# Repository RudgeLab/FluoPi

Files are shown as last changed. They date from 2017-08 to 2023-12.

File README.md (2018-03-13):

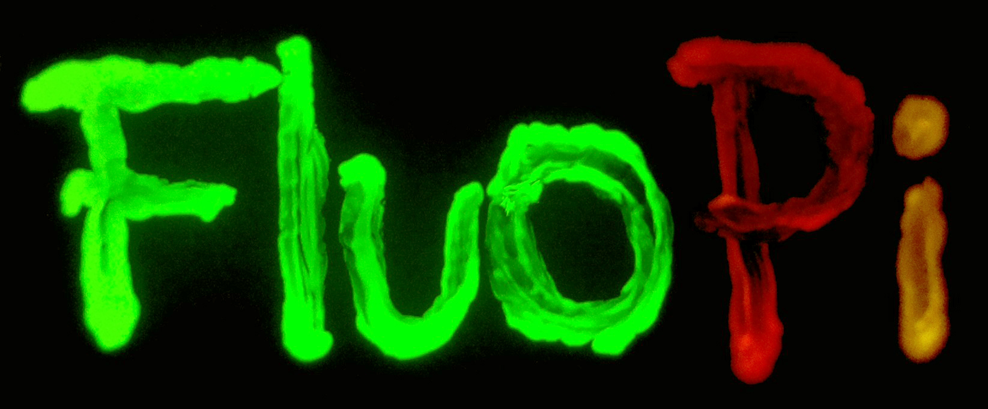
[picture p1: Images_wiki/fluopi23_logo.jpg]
# [][website] 

Hardware design files, code and teaching materials for a low cost and open source fluorescent image registration station.

## Overview

FluoPi is composed of a blue-light transilluminator, an amber acrylic filter and a raspberry camera contained in a black acrylic mainframe. All the hardware is controlled with a Raspberry pi small computer.
With this equipment you are able to:  

* Take images of fluorescent samples ranges from um to cm.
* Perform timelapse assays of up to 3 fluorescent proteins simultaneously
* See electrophoresis gel stained with blue excitable chemicals (such as GelRed or SYBR Safe).

## Getting Started

You can see the full project at [OSF](https://osf.io/dy6p2/)
and a pre-print manuscript at [Biorxiv](https://www.biorxiv.org/content/early/2017/09/27/194324) and peer-reviewed article in [PLoS](http://journals.plos.org/plosone/article?id=10.1371/journal.pone.0187163)

### Prerequisites

To assemble this device you need access to a laser cutter and a 3D printer. You also need a mouse, keyboard and a screen
with HDMI (or hdmi to VGA adaptor) to connect with the Raspberry pi (you can also manage the equipment through SSH or using programs such as [teamviewer](https://pages.teamviewer.com/published/raspberrypi/))

### Installing

All the installation instructions are available on the [wiki page][wiki]

Full documentation and assembly instructions can be found at [Docubricks](http://docubricks.com/viewer.jsp?id=701517893260717056)

### Running the equipment

The equipment has a manual switch and the camera can be controlled with [_camera module commands_](https://www.raspberrypi.org/documentation/usage/camera/raspicam/README.md).
The project includes some python codes (based on [camera python module](https://www.raspberrypi.org/documentation/usage/camera/python/)) to control the hardware:  
* _timelapse.py_ --> to perform timelapse experiments
* _turnON.py_ --> to turn ON the transilluminator
* _turnOFF.py_ --> to turn OFF the transilluminator

### Running the notebooks

Jupyter notebooks are included (Examples/ and Tutorials/) to demonstrate the analysis principles and the use of the fluopi module to analyse time-lapse image data. Sample image data is included in the relevant folders. You can start from these examples, switching the file paths to your data.

## Authors

**Universidad Catolica de Chile**
* Isaac Nuñez - [Prosimio](https://github.com/Prosimio)
* Tamara Matute - [tfmatute](https://github.com/tfmatute)
* Juan Keymner - [Keymer Lab](http://keymerlab.nl/www/?page_id=26)
* Tim Rudge - [Rudge lab](http://rudge-lab.org)
* Fernan Federici - [Federici lab](https://federicilab.org)

[**Backyard Brains Chile**](http://www.backyardbrains.cl/)
* Roberto Pellizzari - [RoHPellizzari](https://github.com/RoHPellizzari)
* Tim Marzullo - [Backyard Brains](http://www.backyardbrains.cl/)

## License

This project is licensed under the MIT License - see the [LICENSE.txt](LICENSE.txt) file for details. Hardware is lincesed under the CERN license.

## FAQs and updates 
Please follow updates, ask questions and check FAQs in this [doc](https://docs.google.com/document/d/1-tSU8xBUZicgM2oZv8TOGw7QUYI85IWkbmjetRthfG8/edit?usp=sharing)

## Acknowledgments

* _Toby Wenzel_ for guidance on Docubricks documentation
* _Tom Baden_  and _Andre Chagas_ for feedback and advice on camera
* _Bernardo Pollak_ for helping out with sequences
* _Douglas Densmore_ for the CIDAR MoClo Parts Kit

* _OpenPlant Fund_ and _Fondecyt_ for providing financial support

[wiki]: https://github.com/SynBioUC/FluoPi/wiki
[website]: https://osf.io/dy6p2/

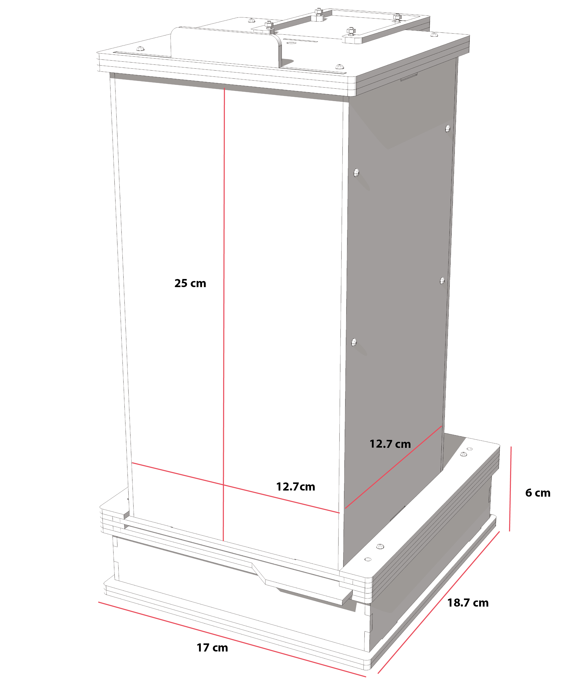
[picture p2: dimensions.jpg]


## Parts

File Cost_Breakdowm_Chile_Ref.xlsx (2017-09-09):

Item | Quantity | Cost Un Chilean Pesos | Cost x1 (USD) | Total cost (USD) | Reference | details
Rapsberry PI model 3 with 16Gb SD card | 1 | $41500 | $62.88 | $62.88 | http://olimex.cl/en_US/shop/product/raspberry-pi-model-3-with-16gb-memory-noobs-system-preloaded-21545?category=415
Power supply RPI | 1 | $8590 | $13.02 | $13.02 | http://olimex.cl/en_US/shop/product/transformador-para-raspberry-pi-5v-2-5amp-21421?category=415&page=2
M3 - 10 mm Length Screw | 20 | $9.81 | $0.01 | $0.30 | www.fijaciones.com (http://www.fijaciones.com/mr/pernos_tuercas_golillas/perno_cocina_cabeza_binding.asp)
M3 - 15 mm Length Screw | 6 | $11.35 | $0.02 | $0.10 | www.fijaciones.com (http://www.fijaciones.com/mr/pernos_tuercas_golillas/perno_cocina_cabeza_binding.asp)
M3 - 20 mm Length Screw | 6 | $5.95 | $0.01 | $0.05 | www.fijaciones.com (http://www.fijaciones.com/mr/pernos_tuercas_golillas/perno_cocina_cabeza_binding.asp)
M3 Hex Nut | 32 | $8.71 | $0.01 | $0.42 | www.tecbolt.cl (http://www.tecbolt.cl/mr/pernos_tuercas_golillas/pdf/tuerca_cocina_hexagonal.pdf)
M4 - 25 mm Length Screw | 6 | $18.90 | $0.03 | $0.17 | www.fijaciones.com (http://www.fijaciones.com/mr/pernos_tuercas_golillas/perno_cocina_cabeza_binding.asp)
M4 - 40 mm Length Screw | 1 | $33.03 | $0.05 | $0.05 | www.fijaciones.com (http://www.fijaciones.com/mr/pernos_tuercas_golillas/perno_cocina_cabeza_binding.asp)
M4 - 50 mm Length Screw | 4 | $31.34 | $0.05 | $0.19 | www.fijaciones.com (http://www.fijaciones.com/mr/pernos_tuercas_golillas/perno_cocina_cabeza_binding.asp)
M4 Hex Nut | 11 | $8.93 | $0.01 | $0.15 | www.tecbolt.cl (http://www.tecbolt.cl/mr/pernos_tuercas_golillas/pdf/tuerca_cocina_hexagonal.pdf)
3D prints (all together) | 1 | $2000 | $3.03 | $3.03 | Calculated based on ABS cost in grams of materials
80 x 50 cm Black Acrylic Plate 3mm | 2 | $12300 | $18.64 | $37.27 | www.norglas.cl/
30 x 30 cm Transparent Acrylic Plate 3mm | 1 | $2315 | $3.51 | $3.51 | www.norglas.cl/
30 x 30 cm Amber Acrylic Plate 3mm | 1 | NA | $7.84 | $7.84 | https://www.mcmaster.com/#catalog/123/3632/=191et4m | 85635K462 Optically Fluorescent Cast Acrylic, 1/8" Thick, 12" X 12", Amber
30 x 30 cm Blue Acrylic Filter 3mm | 1 | NA | $9.34 | $9.34 | http://www.acrylite.net/product/acrylite/en/Pages/default.aspx | ACRYLITE® extruded (FF), sheet, Blue 5C028 GT
Paper Diffusor | 1 | $1000 | $1.52 | $1.52
RPi Camera (B), Adjustable-Focus | 1 | NA | $17.59 | $17.59 | http://www.waveshare.com/product/mini-pc/raspberry-pi/cameras/rpi-camera-b.htm
PCB | 1 | $7500 | $11.36 | $11.36 | https://www.seeedstudio.com
Blue LED | 100 | NA | $0.54 | $54.00 | https://www.superbrightleds.com/moreinfo/through-hole/5mm-blue-led-120-degree-viewing-angle-flat-tipped-1200-mcd/265/
Switch | 1 | $200 | $0.30 | $0.30 | https://www.digikey.com/product-detail/en/zf-electronics/SRB22A2FBBNN/CH755-ND/446021
Power Plug | 1 | $200 | $0.30 | $0.30 | www.casaroyal.cl/Casa/Royal
24V Power Source | 1 | $12990 | $19.68 | $19.68 | www.casaroyal.cl/Casa/Royal
Resistor 330 ohm | 20 | NA | $0.03 | $0.60 | https://www.digikey.com/product-detail/en/stackpole-electronics-inc/CF14JT330R/CF14JT330RCT-ND/1830338
Resistor 1 kohm | 1 | NA | $0.03 | $0.03 | https://www.digikey.com/product-detail/en/stackpole-electronics-inc/CF14JT1K00/CF14JT1K00CT-ND/1830350
Digital Control Cable | 1 | $1000 | $1.52 | $1.52
TIP122 transistor | 1 | $400 | $0.61 | $0.61 | www.casaroyal.cl/Casa/Royal
Total |  |  |  | $245.22

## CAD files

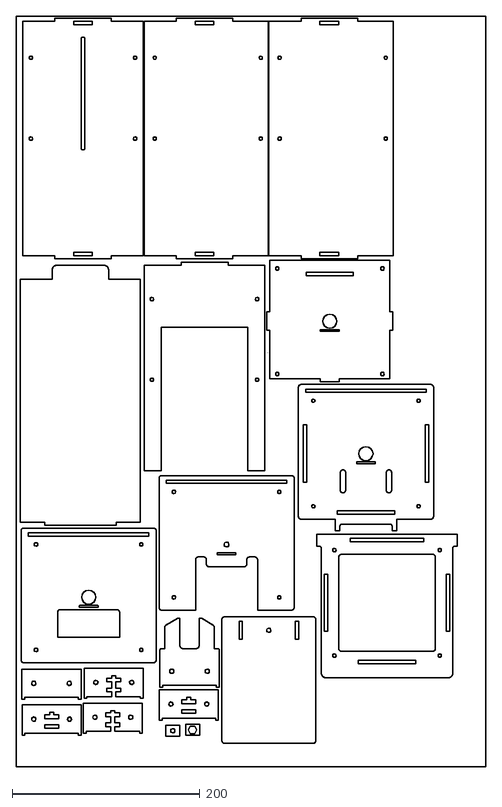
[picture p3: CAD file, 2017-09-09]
Hardware_design_files/2D/ReadytoCut/Fluopi - Black Ac - 3mm - 800x500 mm.dxf
500.0 x 800.0

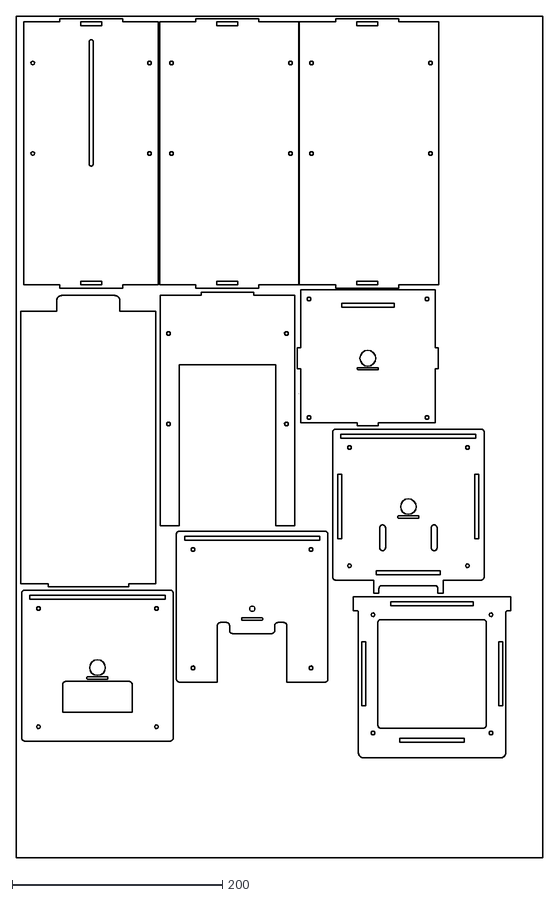
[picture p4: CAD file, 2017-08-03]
Hardware_design_files/2D/single_files/MF6-3 Final Cut - Top Module Black Acrilic.dxf
500.0 x 800.0

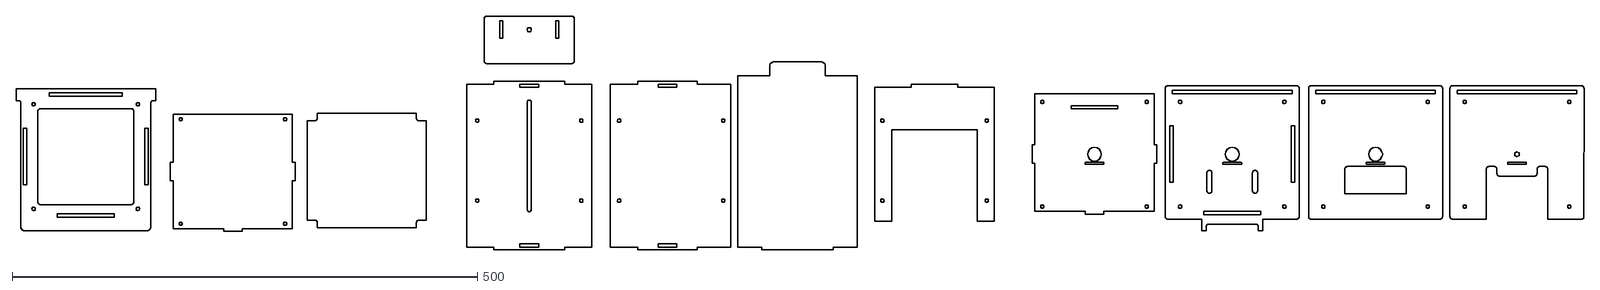
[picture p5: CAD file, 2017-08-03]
Hardware_design_files/2D/single_files/short_version/MF6-3 Final Cut - Short TopMod.dxf
1684.9 x 251.2

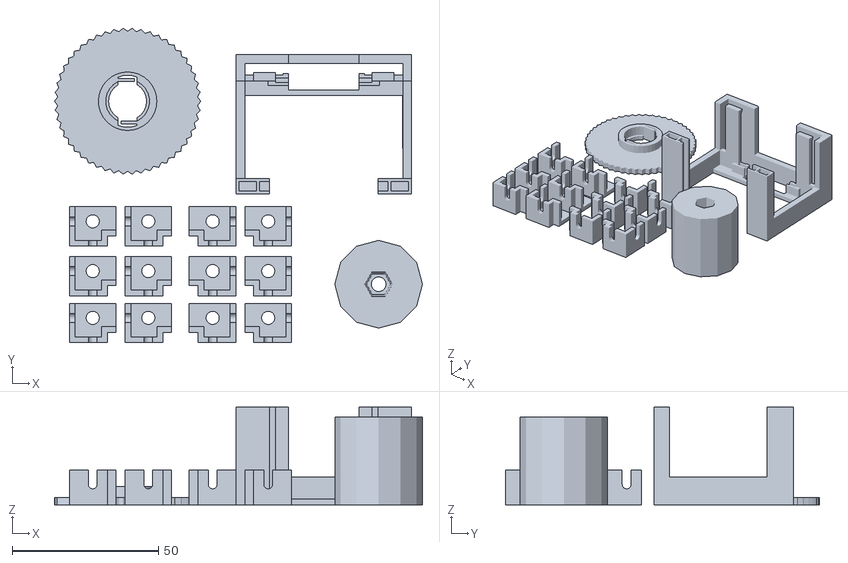
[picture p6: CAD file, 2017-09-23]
Hardware_design_files/3D/Readytoprint/Fluopi - All 3D print parts.stl
125.8 x 107.5 x 33.5

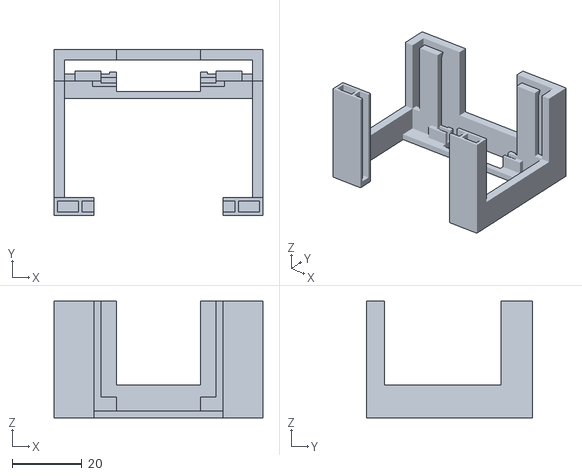
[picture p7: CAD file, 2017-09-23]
Hardware_design_files/3D/single_files/MF6-3 Final Cut - Raspberry Cam Adaptor.stl
60.0 x 47.6 x 33.5

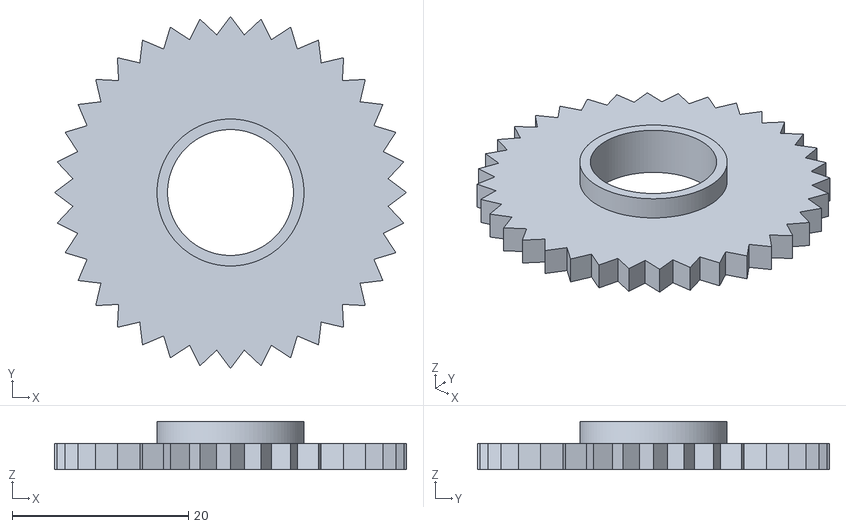
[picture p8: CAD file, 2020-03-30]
PostManuscript_updates_and_FAQs_other_versions/Hardware/STLs/M12_focus_knob.stl
40.0 x 40.0 x 5.50

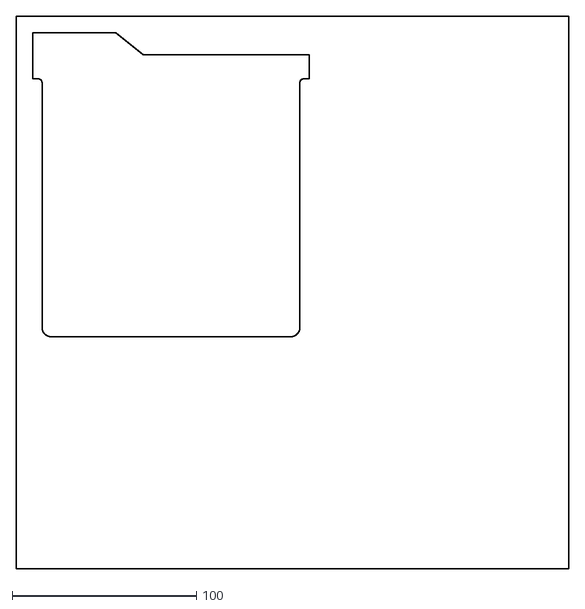
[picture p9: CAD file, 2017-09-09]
Hardware_design_files/2D/ReadytoCut/Fluopi - Blue Ac - 3mm - 300x300 mm.dxf
300.0 x 300.0

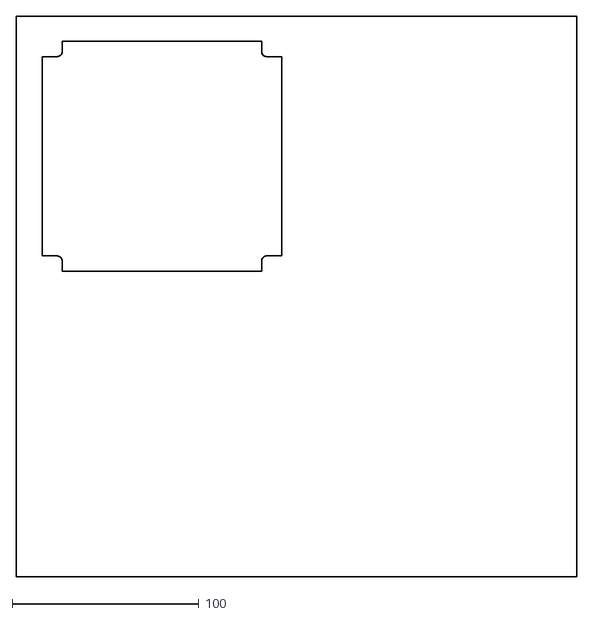
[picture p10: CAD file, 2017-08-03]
Hardware_design_files/2D/single_files/MF6-3 Final Cut - Paper Diffusor.dxf
300.0 x 300.0

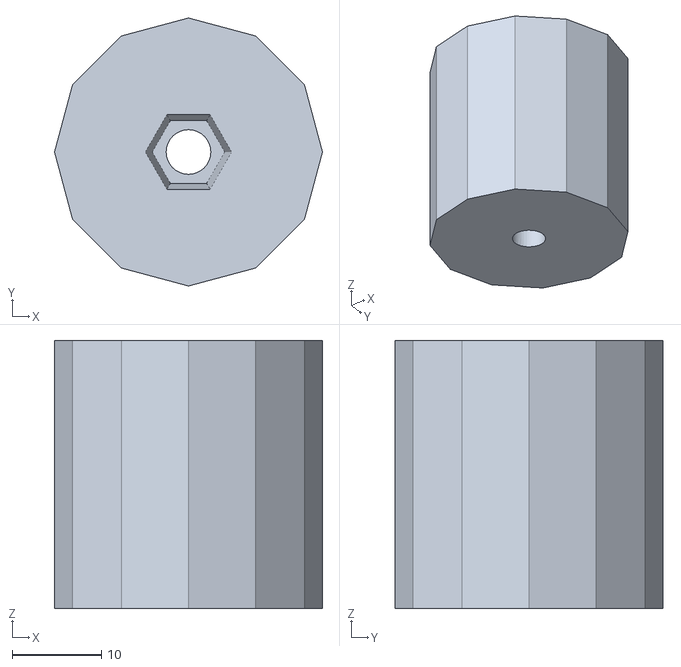
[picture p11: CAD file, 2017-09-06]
Hardware_design_files/3D/single_files/MF6-3 Locking Knob.stl
30.0 x 30.0 x 30.0

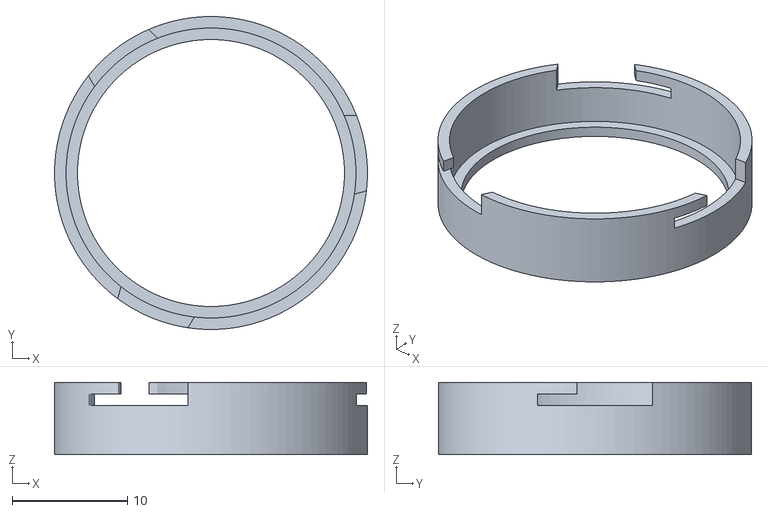
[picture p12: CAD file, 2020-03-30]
PostManuscript_updates_and_FAQs_other_versions/Hardware/STLs/circle_filter_holder.stl
27.2 x 27.2 x 6.30

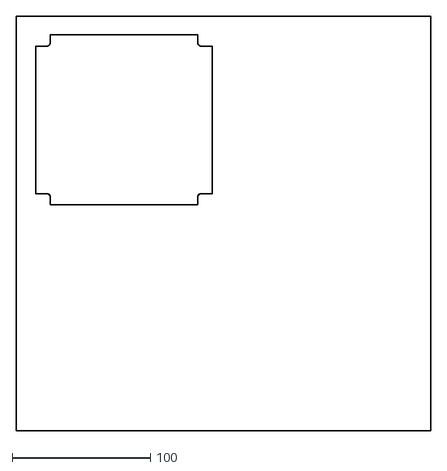
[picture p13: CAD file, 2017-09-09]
Hardware_design_files/2D/ReadytoCut/Fluopi - Paper Diffusor - 300x300 mm.dxf
300.0 x 300.0

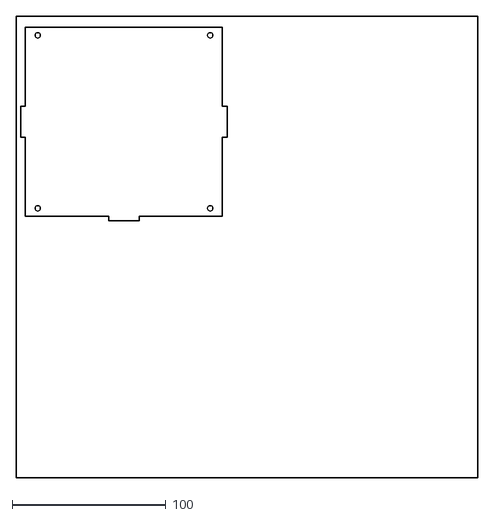
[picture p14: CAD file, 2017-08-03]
Hardware_design_files/2D/single_files/MF6-3 Final Cut - Top Module Transparent Acrilic.dxf
300.0 x 300.0

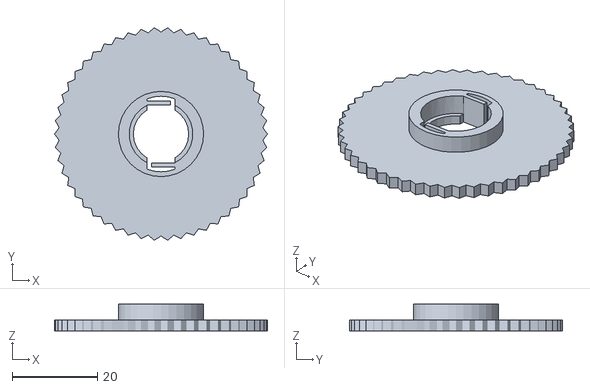
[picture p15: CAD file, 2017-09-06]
Hardware_design_files/3D/single_files/Focus Knob.stl
50.0 x 49.9 x 6.30

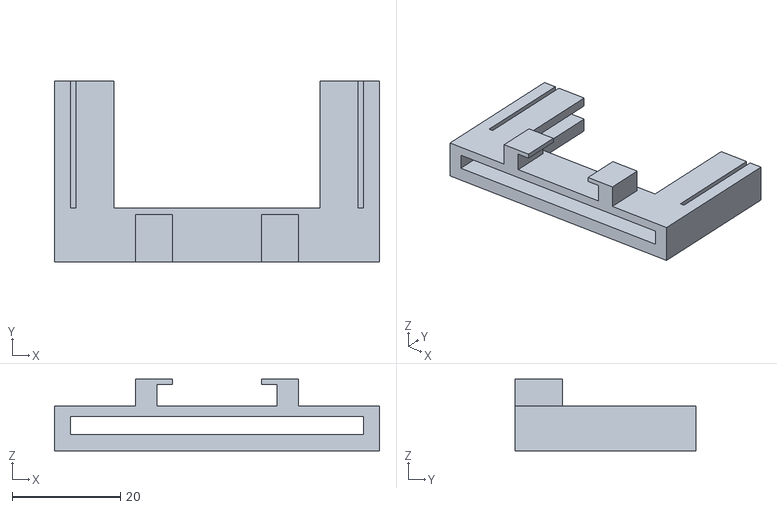
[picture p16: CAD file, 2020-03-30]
PostManuscript_updates_and_FAQs_other_versions/Hardware/STLs/Flat_cam_holder_RPIV2cam.stl
60.0 x 33.5 x 13.2

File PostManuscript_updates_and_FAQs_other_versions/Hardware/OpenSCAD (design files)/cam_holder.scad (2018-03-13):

/*
    Fernán Federici 2017 (CC BY 4.0; https://creativecommons.org/licenses/by/4.0/) 
 
    With this code you can make a camera adapter for RPI camera from waveshare (http://www.waveshare.com/product/mini-pc/raspberry-pi/cameras/rpi-camera-b.htm) and for V2 RPI camera (https://www.raspberrypi.org/products/camera-module-v2/)
 
*/

/////This code needs a lot of clean up and reorganization but it works//////////edits would be very welcome :) ////////////
 
x=60;//frontal width
y=47;//height 33+9+5
z=33.5; // depth
filter_x=43.7;
filter_y=31.4;
filter_z=3;
bed_x=54;
bed_y=3;
bed_z=100;
arm=5;
focus_space=20; // enough distance for lens focus adjustment
holder_x=54;//acrylic bed width to fit into holder
holder_y=3;//acrylic bed thickness to fit into holder, normally 3mm acrylic
$fn=100;
fudge=0.1; // to fix error in rendering leaving thin wall...help me!
int_gap=17.5; 
camera_type=0; //0 for waveshare camera (32x32mm); 1 for V2 RPI camera (25x24x9)
china_spacex= 24.3;
V2_spacex= 18;
waveshare_cam_x=32.2;
waveshare_cam_y=1.5; //thickness
waveshare_cam_z=32.2;
RPIV2_cam_x=25;
RPIV2_cam_y=1.5; //thickness
RPIV2_cam_z=24;


module cam_holder_base() {
    difference(){
    cube([x,y,z], center=true);
           translate([0,(y/2)-arm/2,2]) rotate([90,0,0])  cube([filter_x,filter_y,filter_z], center=true);
           translate([0,0,8])  color("blue") cube([filter_x-4,y+fudge,z*0.9], center=true);
           translate([0,(y/2)-(focus_space/2+arm),0])  color("Red")  cube([(x-arm),focus_space,z+fudge], center=true);
           translate([0,-((y/2)-arm/1.5),0]) color ("pink") cube([holder_x+fudge,holder_y,z+fudge], center=true);
           translate([0,-arm,arm+fudge]) color ("purple")  cube([(x-arm)+fudge,focus_space,(z-arm*2)+fudge], center=true);
           translate([0,-arm*1.5,-arm/2+fudge]) color ("yellow")  cube([int_gap,y/2,(z-arm*2)+fudge], center=true);
           translate([0,-arm*2,-arm/2+fudge]) color ("black")  cube([filter_x-4,arm*2,(z-arm*2)+fudge], center=true);
    }
}
       
module waveshare_cam() {
           translate([0,-((y/2)-arm/.75),0]) color ("red")  cube([china_spacex,arm*1.5,z+fudge], center=true);
           translate([0,-((y/2)-arm/.75),arm/2+fudge]) color ("yellow")  cube([waveshare_cam_x,waveshare_cam_y,z+fudge], center=true);
 }
  
module RPIV2_cam() {
       //difference() {
           //cam_holder_base();
           translate([0,-((y/2)-arm/.75),0]) color ("red")  cube([V2_spacex,arm*1.5,z+fudge], center=true);
           translate([0,-((y/2)-arm/.75),arm/2+fudge]) color ("yellow")  cube([RPIV2_cam_x,RPIV2_cam_y,RPIV2_cam_z+fudge], center=true);
     }     
     
module cam_holder(camera_type) {

     if(camera_type==0)
           difference() {
           cam_holder_base();
               waveshare_cam() ;
           }          
     else 
           difference() {
           cam_holder_base();
               RPIV2_cam();
           }
       }     
cam_holder(1); 

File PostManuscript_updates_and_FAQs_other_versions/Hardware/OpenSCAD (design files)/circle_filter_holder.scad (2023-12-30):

/*
    
    With this code you can make a filter holder to attach it to the lens focus wheel used for the camera in the FluoPi project.
    
    Isaac Núñez 2020 (CC BY 4.0; https://creativecommons.org/licenses/by/4.0/) 
 
*/

////////////////
// Parameters //


ri = 12.6;   //filter radius
side_thick = 1 ;
filter_thick = 3;
filter_free_space = 0.5;
bottom_thick = 0.8;
sheet = 1; // sheet tickness to support the filter

rb = ri-sheet; // internal hole radius
re = ri +side_thick; // External radius

h_fs = filter_thick +filter_free_space + bottom_thick; //base filter support heigh

// HQ camera
r_hq = 15; // HQ camera radius
h_ring = 3; // Height of the ring attached to the camera

// RPI V2 camera


// Clamp support system for waveshare camera
h_clam = 2;
free_clam_space = 10;
angles1 = [0,120,240];
angles2 = [15,135,255];

h_WS = h_fs + h_clam; // for waveshare

////////////////////////////////////

module clam_space(length, wide, thickness, angles){

    for(ang = angles){
       rotate([0,0,ang])
       translate([length/2, 0, 0])
       cube([length, wide, thickness], center = true);
    }
}



////////////////////////
// Create the holder //

module filter_support(h){
    difference(){
    linear_extrude(height = h, center = true, convexity = 10, twist = 0,$fn = 100)
    circle(re);
    
    translate([0,0,bottom_thick])
    linear_extrude(height = h, center = true, convexity = 10, twist = 0,$fn = 100)
    circle(ri);
        
    translate([0,0,-bottom_thick])          linear_extrude(height = h, center = true, convexity = 10, twist = 0,$fn = 100)
    circle(rb);
    }
}

module fsup_WS_clamp(h){
    difference(){
        
        filter_support(h);
        
        // Clamp system
        translate([0,0,h/2-h_clam/2 - h_clam/4]) 
        clam_space(re*1.5, free_clam_space ,h_clam/2, angles1);

        translate([0,0,h/2-0.8*h_clam/2.1])  
        intersection() {

            clam_space(re*1.5, free_clam_space ,h_clam*0.8, angles1);

            clam_space(re*1.5, free_clam_space ,h_clam*0.8, angles2);
        }
    }
}

module fsup_HQ(h){
    h_total = h + bottom_thick + h_ring;
    
    difference(){
        union(){
            filter_support(h);
            
            //union ring
            translate([0,0,(h-bottom_thick)/2])
            cylinder(h=bottom_thick, r=r_hq+side_thick, $fn=100, center =true);
            
            //ring attached to HQ camera
            translate([0,0,(h+h_ring)/2])
            difference(){
                cylinder(h=h_ring, r=r_hq+side_thick, $fn=100, center =true);
                cylinder(h=h_ring, r=r_hq, $fn=100, center =true);
            }
            }
    translate([0,0,bottom_thick+h/2])          
    cylinder(h=h_total, r=ri, $fn=100, center =true);  
    }

}

module fsup_rpiv2(h){
    union(){
        filter_support(h);
    
    }
}

// Uncomment the module you wanna generate
//fsup_WS_clamp(h_WS);
//filter_support(h_WS);
fsup_HQ(h_fs);

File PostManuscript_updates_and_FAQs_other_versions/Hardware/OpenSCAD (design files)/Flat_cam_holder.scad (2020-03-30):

/*
    With this code you can make a camera holder for RPI camera from waveshare (http://www.waveshare.com/product/mini-pc/raspberry-pi/cameras/rpi-camera-b.htm) or for V2 RPI camera (https://www.raspberrypi.org/products/camera-module-v2/)
    
    The code was modified from Fernán Federici 2017 version.
    
    This is licensed under the Creative Commons - Attribution license (CC BY 4.0)
    Isaac Núñez 2020.
 
*/

///////////////////////
// Fluopi parameters

holder_x=54;//acrylic bed width to fit into holder
holder_z=3*1.1;//acrylic bed thickness to fit into holder, normally 3 mm acrylic. 1.1 correction factor applied to surpass acrylic manufacture variations.

////////////////////////
// Defined by the user

// Base holder parameters

sca_thick_up = 3; // holder scafold thickness
sca_thick_side = 3; // holder scafold thickness
sca_thick_down = 2; // holder scafold thickness
sca_deep = 10;  // holder scafold back deep, it have to be shorter than the distance to the screws in the camera PCB (14 mm aprox)
sca_arms_width = 11; // holder scafold arms width

sca_arms_space = 1;  // space attach relaxation


sca_trans = (sca_thick_up - sca_thick_down)/2; // translate the holder space to achieve the desired up and down thicknes

scafold_x = holder_x + 2*sca_thick_side;
scafold_y = 33.5; // depth
scafold_z = holder_z + sca_thick_up + sca_thick_down;


//camera holder parameters

side_thick = 2; //side support thickness
bottom_thick = 1; // bottom support thickness
back_thick = 2; // back support thickness

/////////////////////
//  Camera details:

////////////////////////////////
// Waveshare Chinesse camera //
///////////////////////////////
waveshare_cam_x=32.2 + 1; // 1mm of error
waveshare_cam_y=32.2; 
waveshare_cam_z=1.5*1.1;//thickness
WS_hold_x = 5.1 - 0.3;    // space between border and cable conector. 0.3 the security factor
WS_hold_y = 4.5 - 0.3;  // space between border and resistor. 0.3 the security factor

///////////////////
// RPI V2 camera //
///////////////////

RPIV2_cam_x = 25 + 1 ; // 1mm of error
RPIV2_cam_y = 24; 
RPIV2_cam_z = 1 + 0.1; // PCB thickness, 0.1 mm of error
RPIV2_connec_x = 22; // cable conector length
RPIV2_connec_z = 2.7+ 0.1; // cable conector thikness, 0.1 mm error

RPIV2_sensor_x = 16 + 0.5; // sensor base length (8.5 mm) or adaptor lenght + 0.5 mm error

V2_hold_x =(RPIV2_cam_x - RPIV2_sensor_x)/2 - 0.3;    // space between camera border and sensor base. 0.3 the security factor
V2_hold_y = 7 - 0.2;  // space between border and PCB first obstacle (sensor base or electronic componentes). 0.2 security value.


module cam_holder_base() {
    
    difference(){
    cube([scafold_x,scafold_y,scafold_z], center=true);
     translate([0,0,sca_trans])cube([holder_x,scafold_y*1.1,holder_z], center=true);
     translate([0,sca_deep/2,0])cube([scafold_x - 2*sca_arms_width,scafold_y - sca_deep,scafold_z], center=true);
     translate([holder_x/2-sca_arms_space/2,sca_deep/2,scafold_z/2])cube([sca_arms_space,scafold_y - sca_deep,scafold_z], center=true);
     translate([-holder_x/2+sca_arms_space/2,sca_deep/2,scafold_z/2])cube([sca_arms_space,scafold_y - sca_deep,scafold_z], center=true);
        
        }      
}

module camera_mount(camera){

    if(camera == "waveshare"){
            cam_x = waveshare_cam_x;
            cam_y = waveshare_cam_y;
            cam_z = waveshare_cam_z;
            hold_x = WS_hold_x;
            hold_y = WS_hold_y;
    
        support_z = cam_z+bottom_thick;
        support_y = hold_y + back_thick;
        translate([0,-scafold_y/2 + support_y/2,scafold_z/2+support_z/2])difference(){cube([cam_x+2*side_thick,support_y,support_z], center=true);
            translate([0,back_thick/2,-bottom_thick/2])cube([cam_x,hold_y,cam_z], center=true);
            translate([0,0,0])cube([cam_x - 2*hold_x,support_y,support_z], center=true);
    }
    }
    
    else if(camera == "RPIV2"){
            cam_x = RPIV2_cam_x;
            cam_y = RPIV2_cam_y;
            cam_z = RPIV2_cam_z;
            hold_x = V2_hold_x;
            hold_y = V2_hold_y;
            base_space = RPIV2_connec_x+0.2;
         
    support_z = cam_z+bottom_thick + RPIV2_connec_z;
    support_y = hold_y + back_thick;
    translate([0,-scafold_y/2 + support_y/2,scafold_z/2+support_z/2])difference(){cube([cam_x+2*side_thick,support_y,support_z], center=true);
        translate([0,back_thick/2,-bottom_thick/2 + RPIV2_connec_z/2])cube([cam_x,hold_y,cam_z], center=true); // camera PCB hole
        translate([0,0,-bottom_thick/2])cube([base_space,support_y,support_z-bottom_thick], center=true); // base hole
                translate([0,0,(support_z-bottom_thick)/2])cube([RPIV2_sensor_x,support_y,bottom_thick], center=true); // camera hole
    }
    }
    
}


cam_holder_base();

//uncomment the one you pretend to use

camera_mount("RPIV2");
//camera_mount("waveshare");

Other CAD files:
Hardware_design_files/2D/ReadytoCut/Fluopi - Transp Ac - 3mm - 300x300 mm.dxf
Hardware_design_files/2D/single_files/MF6-3 Final Cut - Dimensiones.dxf
Hardware_design_files/3D/single_files/MF6-3 Final Cut - Spacer L.stl
PostManuscript_updates_and_FAQs_other_versions/Hardware/STLs/Flat_cam_holder_WScam.stl
PostManuscript_updates_and_FAQs_other_versions/Hardware/OpenSCAD (design files)/Focus_knob_FilterAttach.scad
Hardware_design_files/2D/ReadytoCut/Fluopi - Amber Ac - 3mm - 300x300 mm.dxf
Hardware_design_files/2D/single_files/MF6-3 Final Cut - Filter Amber Acrilic.dxf
Hardware_design_files/2D/single_files/MF6-3 Final Cut - Filter Blue Acrilic.dxf
Hardware_design_files/2D/single_files/MF6-3 Final Cut - Raspberry Adaptor Acrilic.dxf
Hardware_design_files/2D/single_files/MF6-3 Final Cut - Vert Bed Module Black Acrilic.dxf
Hardware_design_files/3D/single_files/MF6-3 Final Cut - Spacer R.stl
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

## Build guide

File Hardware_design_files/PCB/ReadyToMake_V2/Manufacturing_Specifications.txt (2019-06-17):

Manufacturing specifications:

PCB size: ~ 170 mm x 125 mm 
Track width: 1.0 mm
N° layers: 2
Material: FR-4
Glass Transition Temperature: TG 130-140
Thickness: 1.6 mm
min Track/Spacing: 6/6mil
Min Hole size: 1.0 mm (choose something lower than 1.0 mm)
SilkScreen: White
Finished Copper: bigger than 1 oz Cu

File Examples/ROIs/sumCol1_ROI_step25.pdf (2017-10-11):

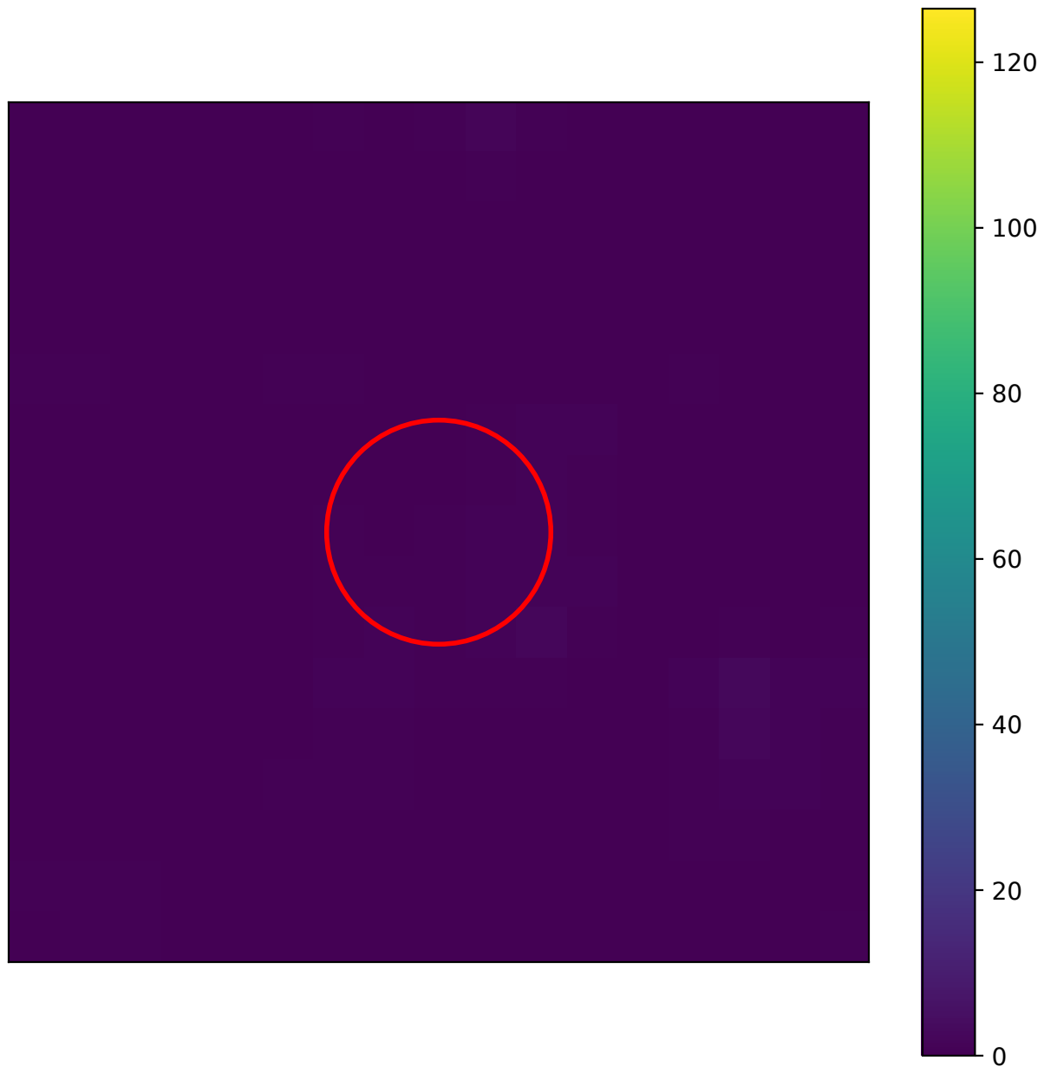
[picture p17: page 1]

0

20

40

60

80

100

120

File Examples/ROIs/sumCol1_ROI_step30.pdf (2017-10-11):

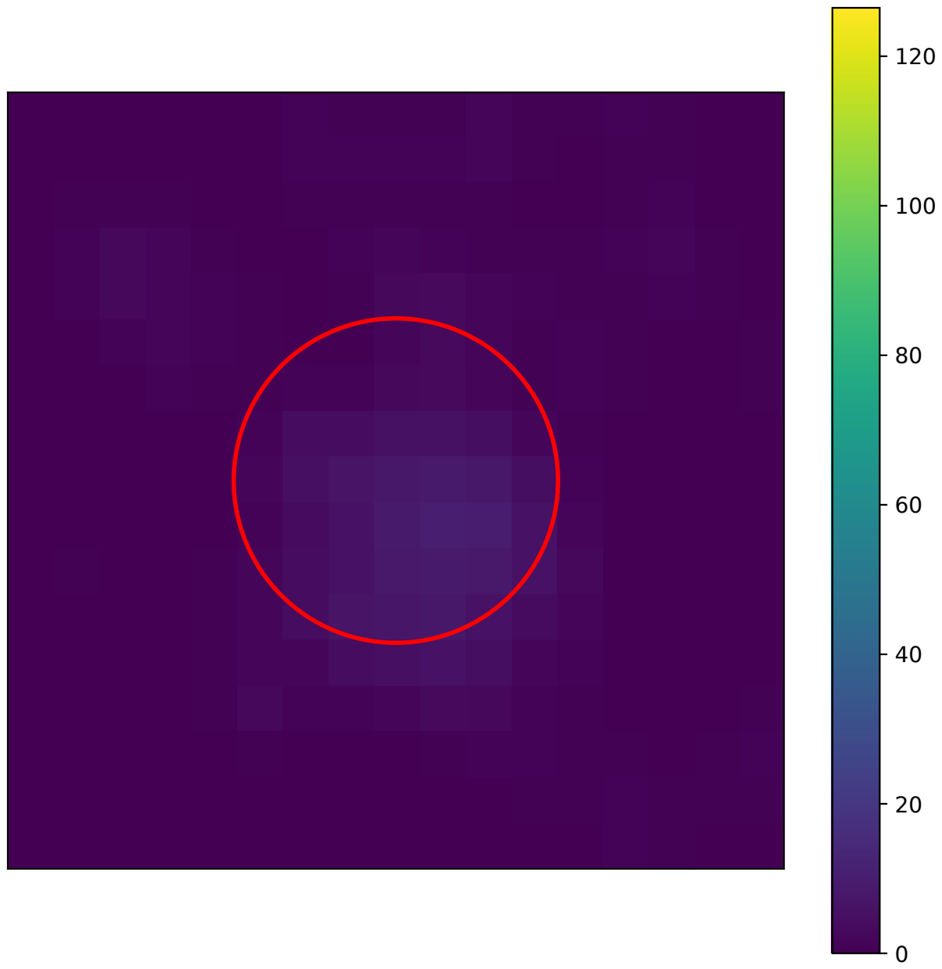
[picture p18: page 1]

0

20

40

60

80

100

120

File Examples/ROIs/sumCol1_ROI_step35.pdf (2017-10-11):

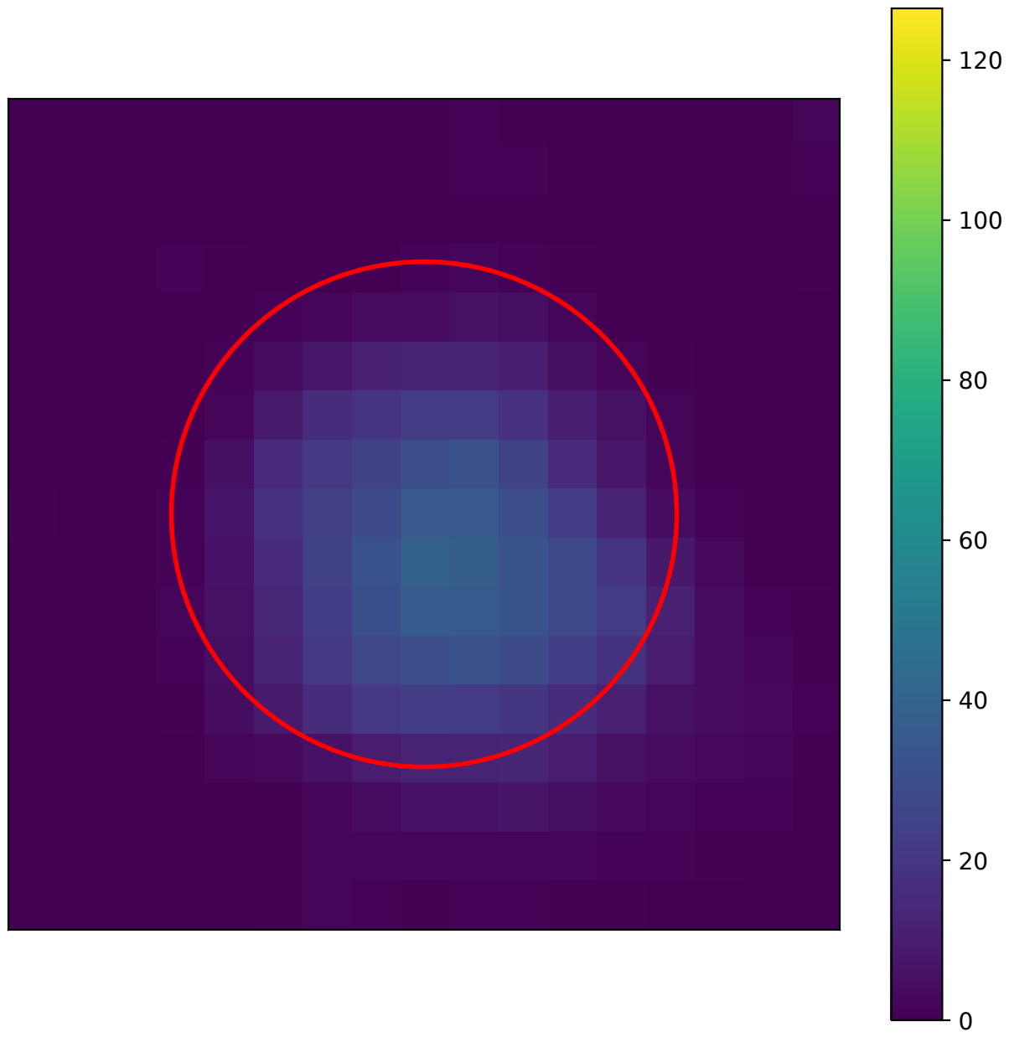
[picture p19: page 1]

0

20

40

60

80

100

120

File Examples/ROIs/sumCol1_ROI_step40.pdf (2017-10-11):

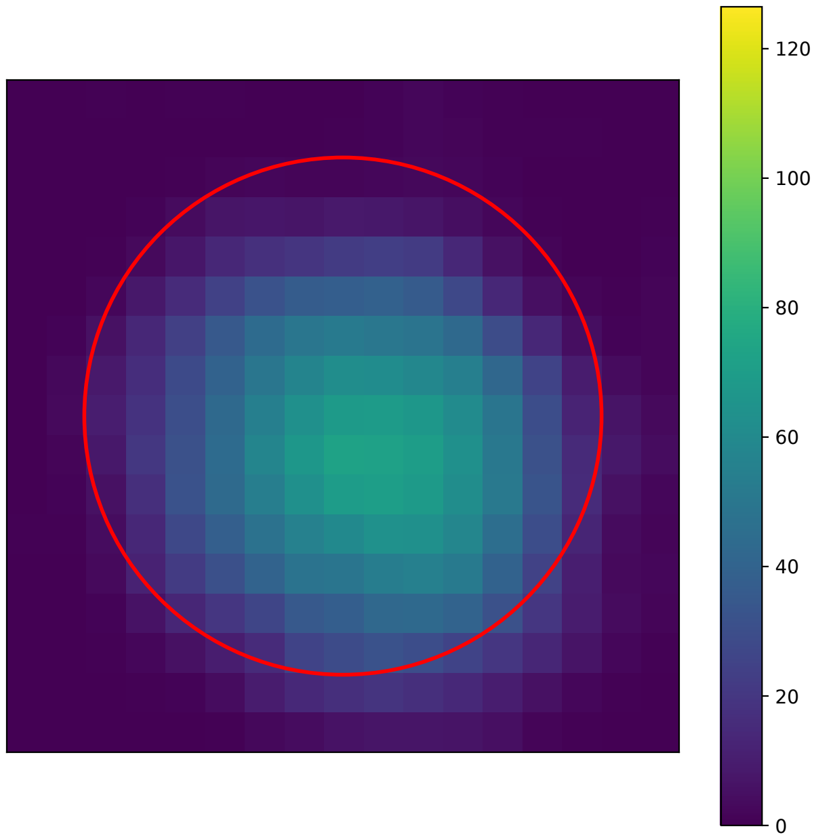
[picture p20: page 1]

0

20

40

60

80

100

120

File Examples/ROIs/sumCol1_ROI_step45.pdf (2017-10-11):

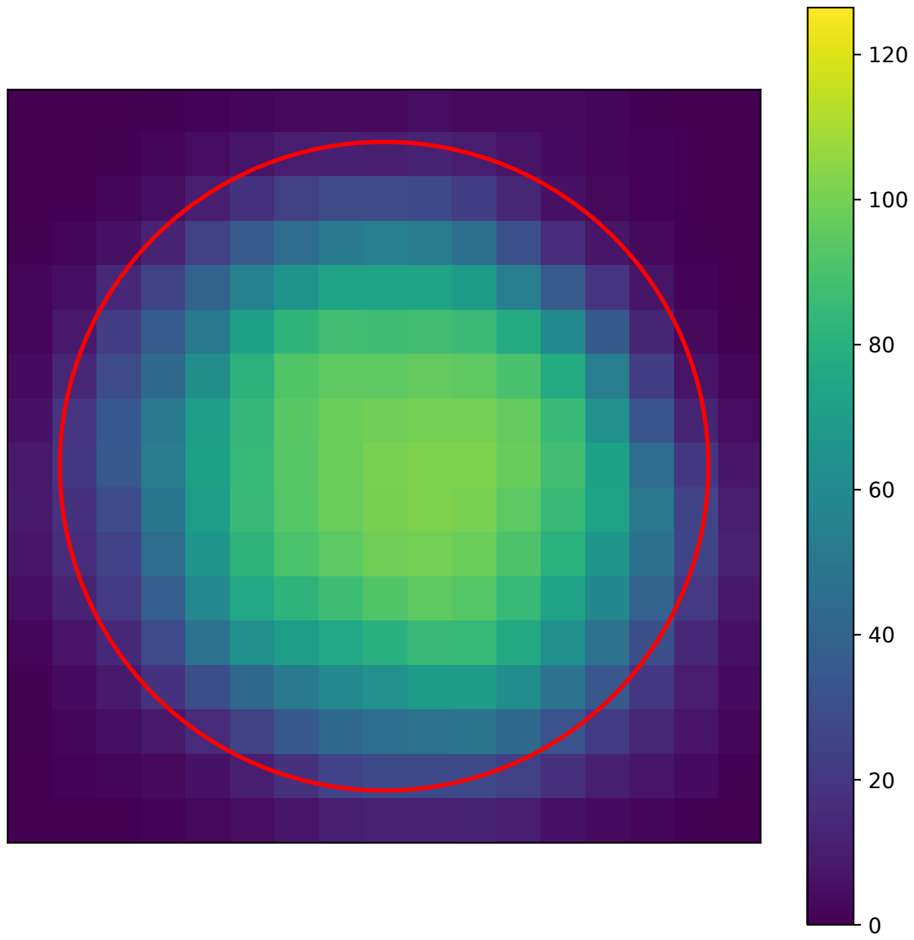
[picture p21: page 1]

0

20

40

60

80

100

120

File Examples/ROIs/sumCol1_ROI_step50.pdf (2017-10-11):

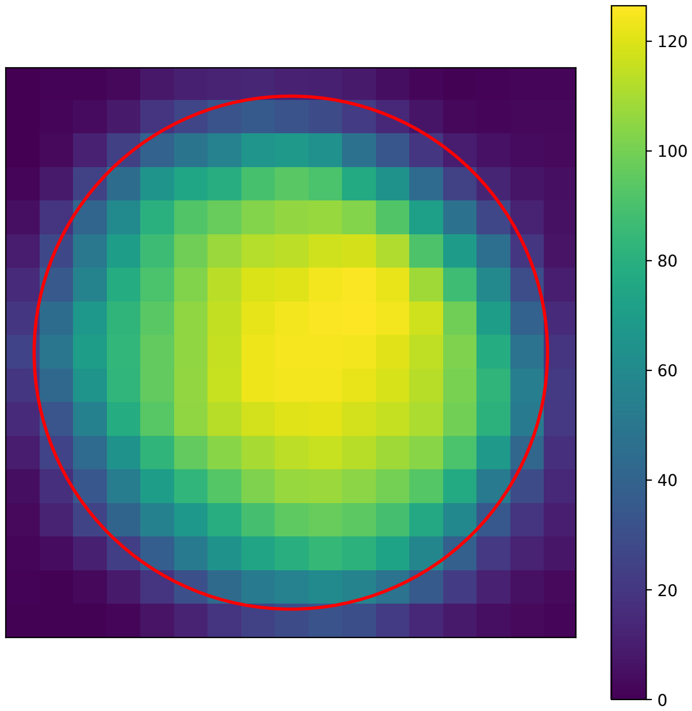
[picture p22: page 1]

0

20

40

60

80

100

120

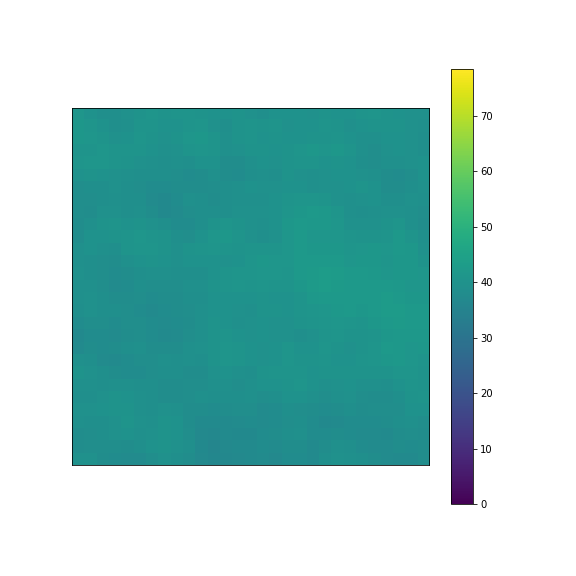
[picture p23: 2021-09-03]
FluOpti/ROIs/TL_3_09_19/White/Col12_ROI_step0.png

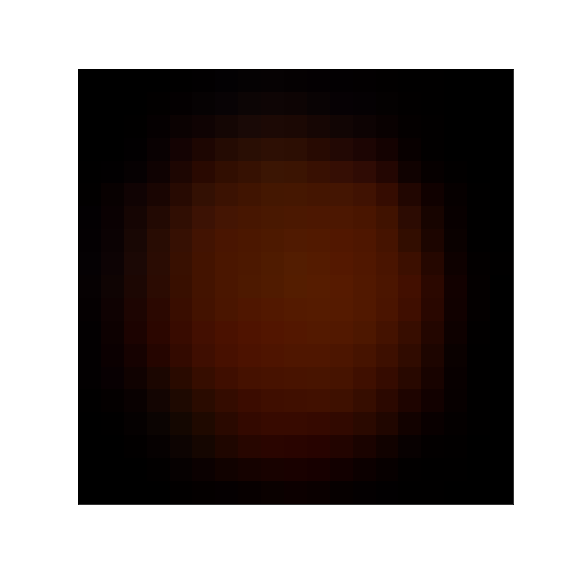
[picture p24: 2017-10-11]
Examples/ROIs/Col66_ROI_step45.png

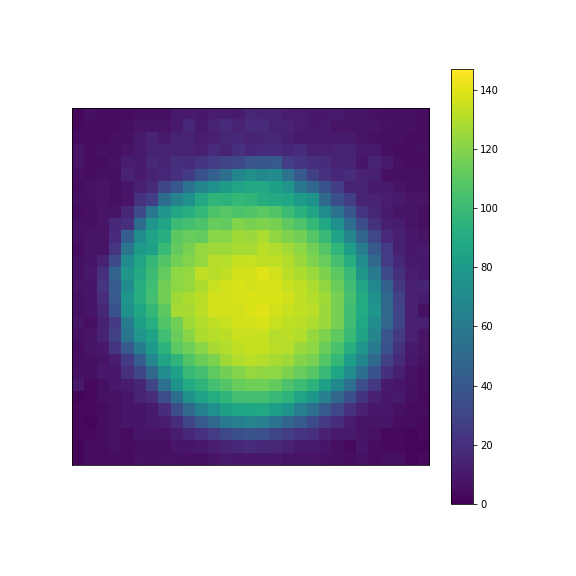
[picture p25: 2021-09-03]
FluOpti/ROIs/TL_3_09_19/Raw3/Col6_ROI_step36.png

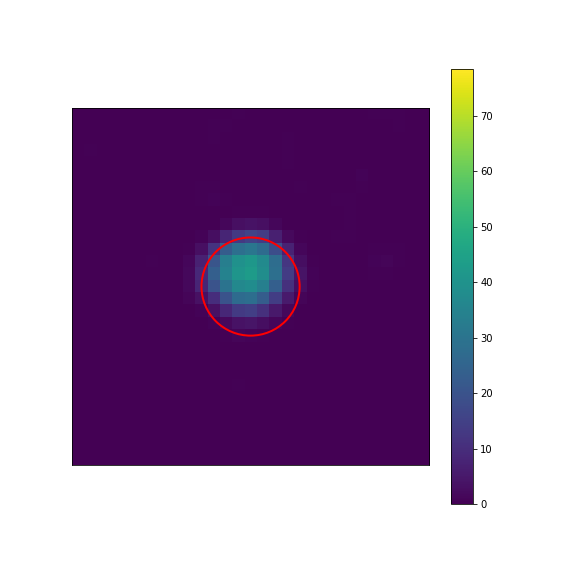
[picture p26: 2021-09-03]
FluOpti/ROIs/TL_3_09_19/White/sumCol4_ROI_step18.png

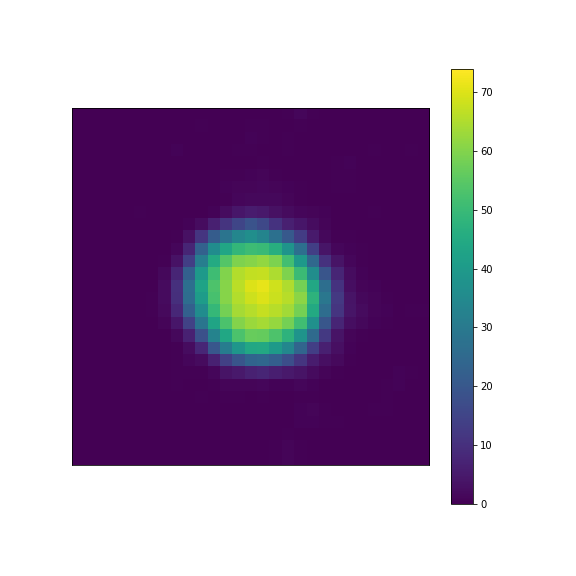
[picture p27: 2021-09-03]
FluOpti/ROIs/TL_3_09_19/White/Col3_ROI_step36.png

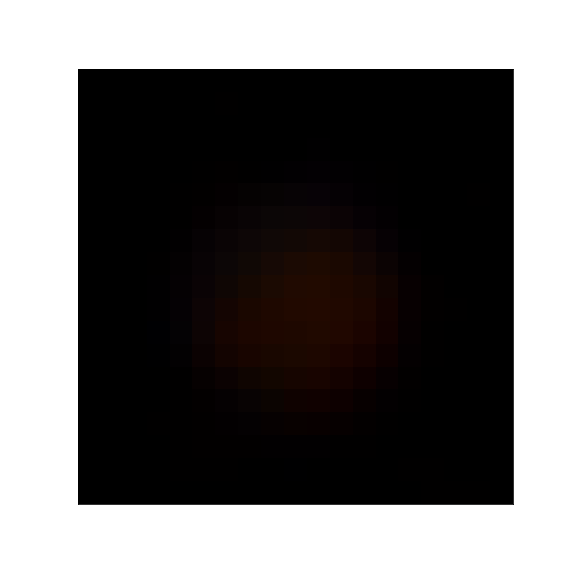
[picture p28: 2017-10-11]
Examples/ROIs/Col66_ROI_step35.png

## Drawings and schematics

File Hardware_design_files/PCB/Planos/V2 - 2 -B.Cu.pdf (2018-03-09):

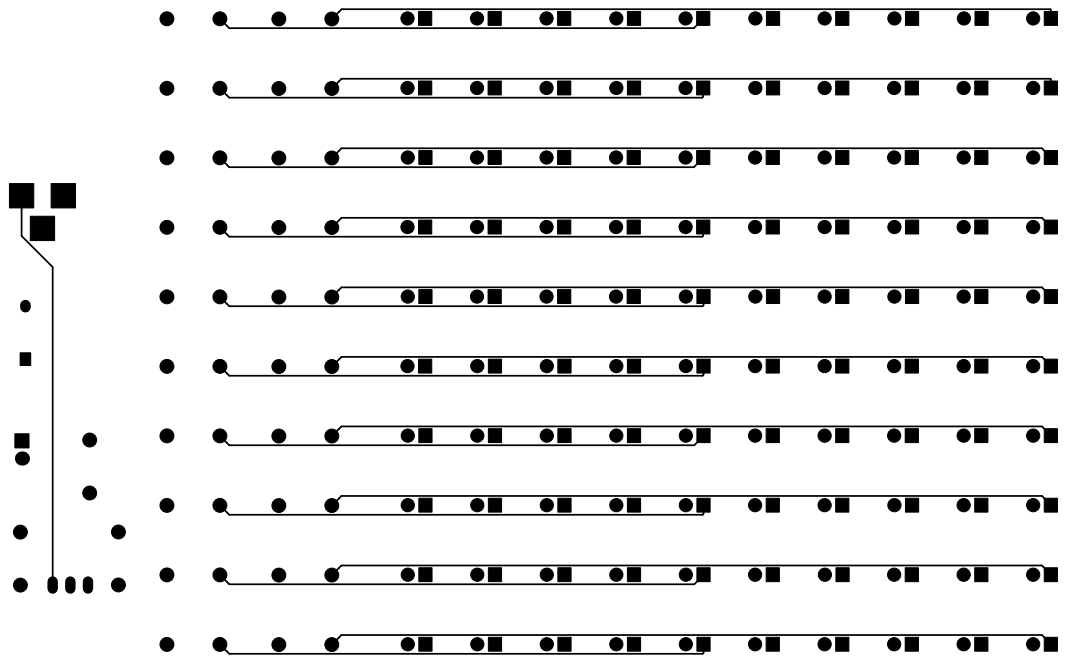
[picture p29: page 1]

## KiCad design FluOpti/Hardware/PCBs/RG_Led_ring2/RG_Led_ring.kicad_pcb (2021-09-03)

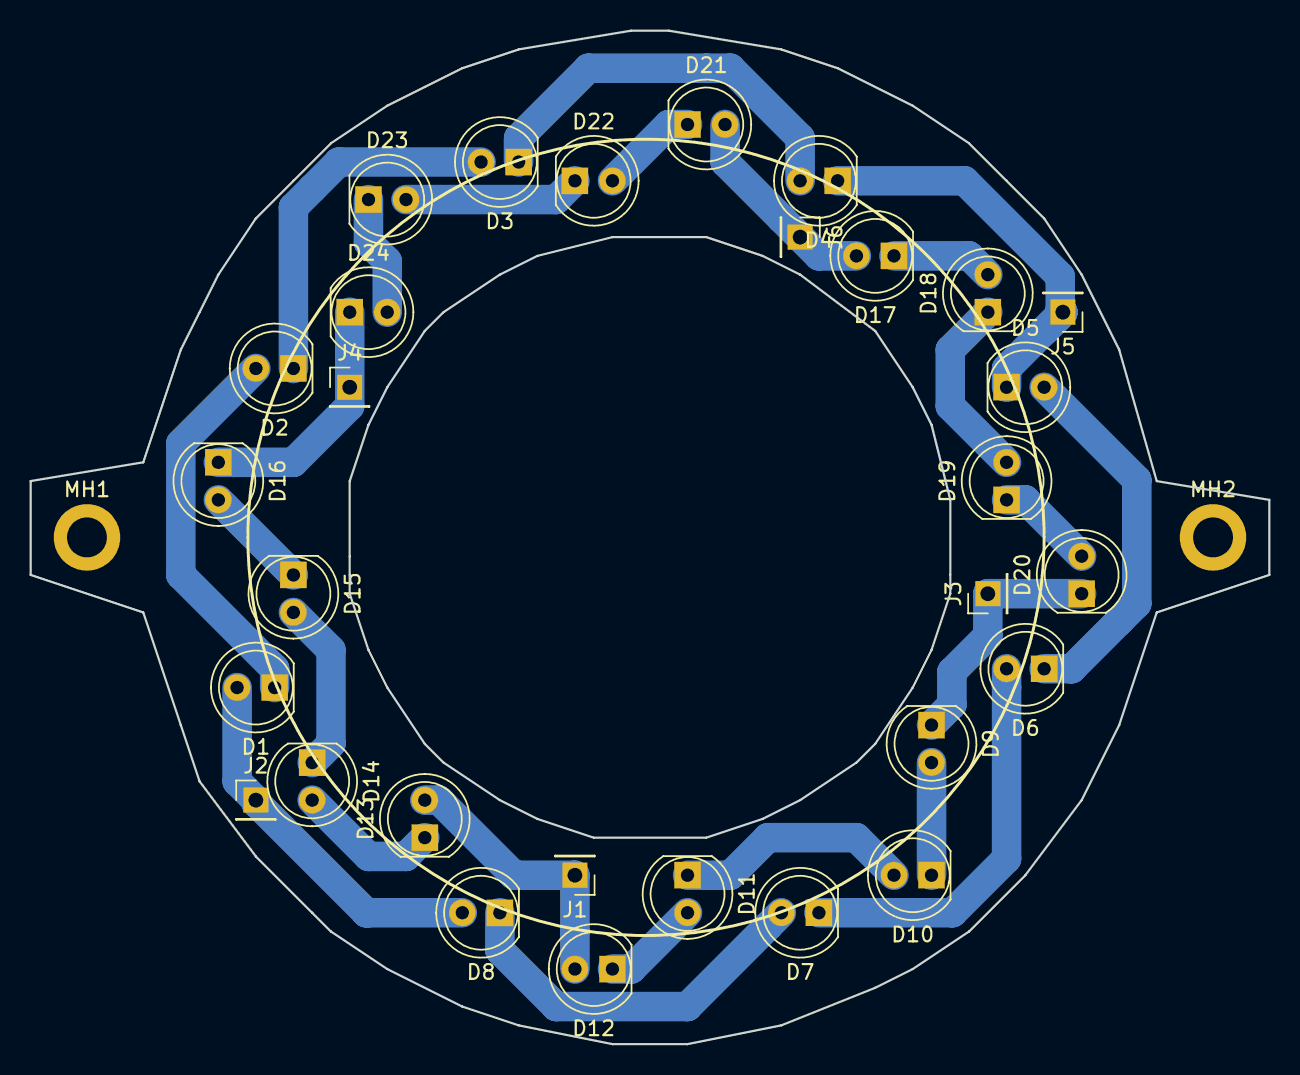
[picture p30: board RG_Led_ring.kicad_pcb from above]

Board: 2 copper layers, 83.8 x 68.6 mm, 32 parts (0 on the bottom side), 24 nets.

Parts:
D1, D2, D3, D4, D5, D6, D7, D8, D9, D10, D11, D12, D13, D14, D15, D16, D17, D18, D19, D20, D21, D22, D23, D24: LED; LED_D5.0mm_FlatTop
J1, J2, J3, J4, J5, J6: Conn_01x01_Female; PinHeader_1x01_P2.54mm_Vertical
MH1, MH2: MountingHole; MountingHole_2.7mm_M2.5_ISO14580_Pad

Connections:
unnamed: D1.1, D2.2
unnamed: D1.2, D8.2, J2.1
unnamed: D2.1, D3.2
unnamed: D3.1, D4.2
unnamed: D4.1, D5.1, J5.1
unnamed: D5.2, D6.1
unnamed: D6.2, D7.1
unnamed: D7.2, D8.1
unnamed: D9.2, D10.1
unnamed: D10.2, D11.1
unnamed: D11.2, D12.1
unnamed: D12.2, D13.2, J1.1
unnamed: D13.1, D14.2
unnamed: D14.1, D15.2
unnamed: D15.1, D16.2
unnamed: D16.1, D24.1, J4.1
unnamed: D17.1, D18.2
unnamed: D17.2, D21.2, J6.1
unnamed: D18.1, D19.2
unnamed: D19.1, D20.2
unnamed: D9.1, D20.1, J3.1
unnamed: D21.1, D22.2
unnamed: D22.1, D23.2
unnamed: D23.1, D24.2

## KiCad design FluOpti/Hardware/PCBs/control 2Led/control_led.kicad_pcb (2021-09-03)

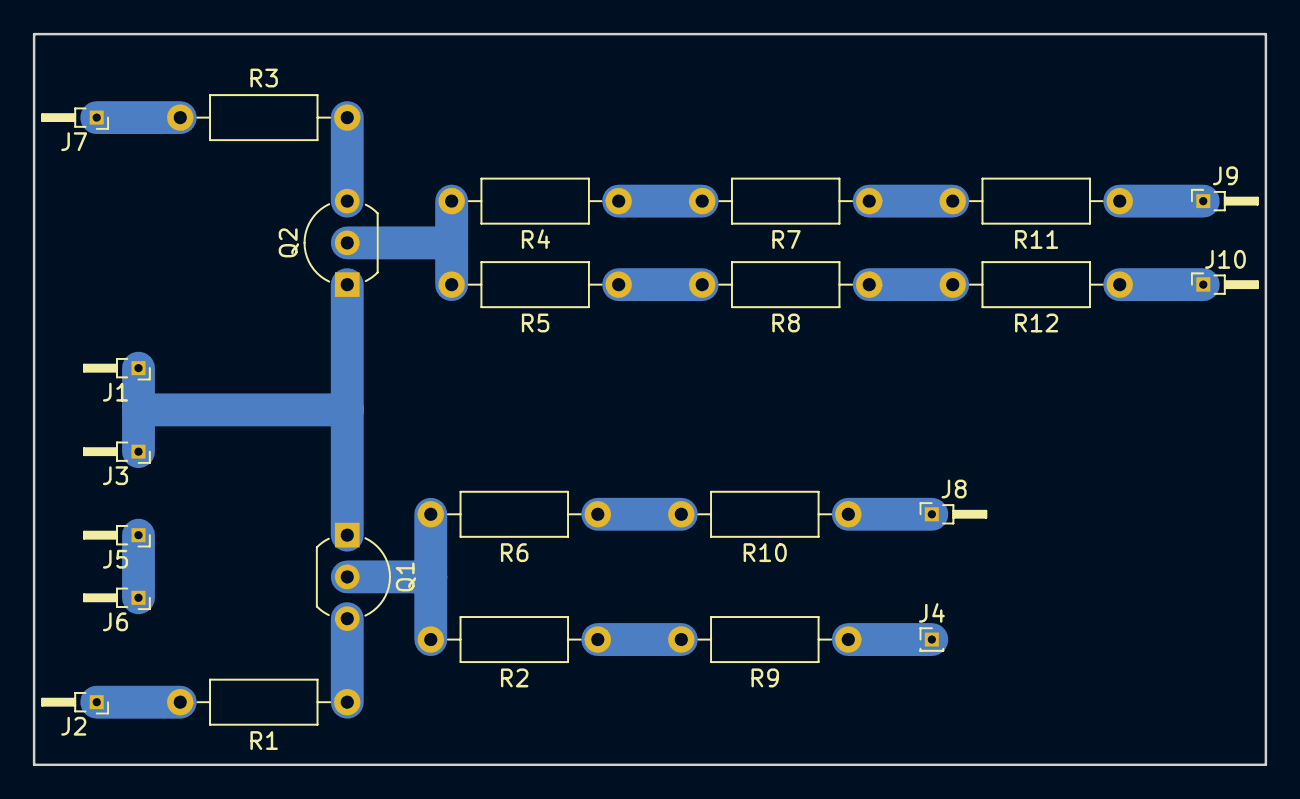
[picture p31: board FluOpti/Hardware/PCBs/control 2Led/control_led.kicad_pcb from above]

Board: 2 copper layers, 74.9 x 44.5 mm, 24 parts (0 on the bottom side), 18 nets.

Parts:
J1, J2, J3, J5, J6, J7, J8, J9, J10: Conn_01x01_Female; PinHeader_1x01_P1.00mm_Horizontal
J4: Conn_01x01_Female; PinHeader_1x01_P1.00mm_Vertical
Q1: PN2222A; TO-92_Inline_Wide
Q2: 2N3904; TO-92_Inline_Wide
R1, R2, R3, R4, R5, R6, R7, R8, R9, R10, R11, R12: R; R_Axial_DIN0207_L6.3mm_D2.5mm_P10.16mm_Horizontal

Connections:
unnamed: J1.1, J3.1, Q1.1, Q2.1
unnamed: J2.1, R1.2
unnamed: J4.1, R9.1
unnamed: J5.1, J6.1
unnamed: J7.1, R3.1
unnamed: J8.1, R10.1
unnamed: J9.1, R11.1
unnamed: J10.1, R12.1
unnamed: Q1.2, R2.2, R6.2
unnamed: Q1.3, R1.1
unnamed: Q2.2, R4.2, R5.2
unnamed: Q2.3, R3.2
unnamed: R2.1, R9.2
unnamed: R4.1, R7.2
unnamed: R5.1, R8.2
unnamed: R6.1, R10.2
unnamed: R7.1, R11.2
unnamed: R8.1, R12.2

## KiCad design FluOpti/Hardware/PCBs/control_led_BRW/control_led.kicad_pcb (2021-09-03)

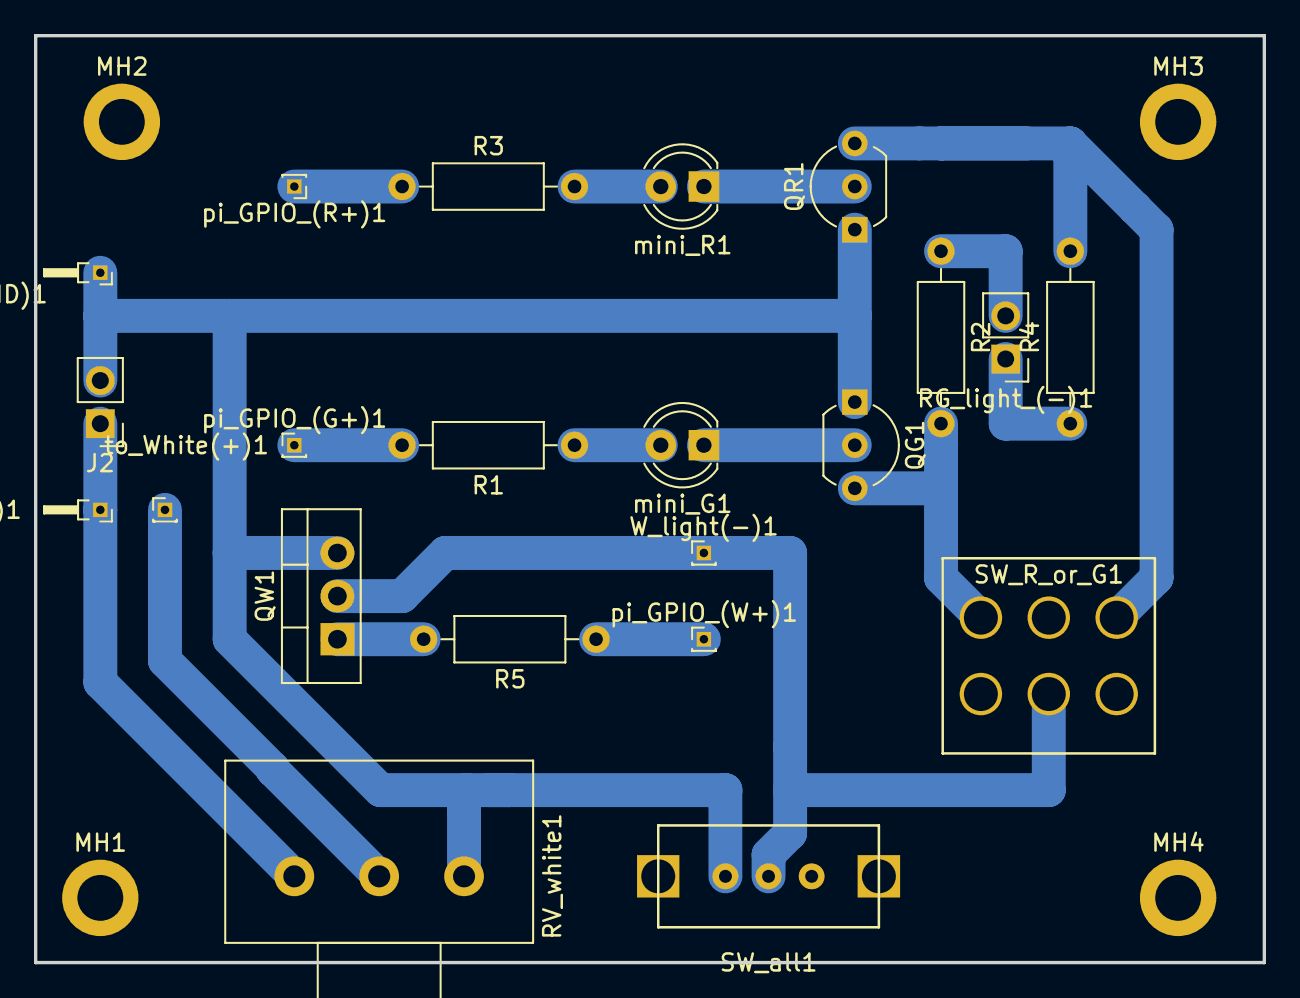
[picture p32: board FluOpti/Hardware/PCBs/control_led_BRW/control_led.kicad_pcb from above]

Board: 2 copper layers, 72.4 x 54.6 mm, 26 parts (0 on the bottom side), 16 nets.

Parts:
J2: to power supply V(-)(+); PinHeader_1x02_P2.54mm_Vertical
MH1, MH2, MH3, MH4: MountingHole; MountingHole_2.7mm_M2.5_ISO14580_Pad
QG1: 2N3904; TO-92_Inline_Wide
QR1: 2N3904; TO-92_Inline_Wide
QW1: TIP122; TO-220-3_Vertical
R1, R2, R3, R4, R5: R; R_Axial_DIN0207_L6.3mm_D2.5mm_P10.16mm_Horizontal
RG_light_(-)1: Conn_01x02_Female; PinHeader_1x02_P2.54mm_Vertical
RV_white1: R_POT; Potentiometer_Alps_RK163_Single_Horizontal
SW_R_or_G1: SW_DPDT_x2; SW_KNX_2_12,5x11,5_P4
SW_all1: SW_DIP_x01; Switch_THT_13.0x6.0_P2.56
W_light(-)1: Conn_01x01_Female; PinHeader_1x01_P1.00mm_Vertical
mini_G1: LED; LED_D4.0mm
mini_R1: LED; LED_D4.0mm
pi_GPIO_(G+)1: Conn_01x01_Female; PinHeader_1x01_P1.00mm_Vertical
pi_GPIO_(R+)1: Conn_01x01_Female; PinHeader_1x01_P1.00mm_Vertical
pi_GPIO_(W+)1: Conn_01x01_Female; PinHeader_1x01_P1.00mm_Vertical
to(Pi_GND)1: Conn_01x01_Female; PinHeader_1x01_P1.00mm_Horizontal
to_RG_(+)1: Conn_01x01_Female; PinHeader_1x01_P1.00mm_Horizontal
to_White(+)1: Conn_01x01_Female; PinHeader_1x01_P1.00mm_Vertical

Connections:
unnamed: J2.1, RV_white1.1, to_RG_(+)1.1
unnamed: J2.2, QG1.1, QR1.1, QW1.3, RV_white1.3, SW_all1.1, to(Pi_GND)1.1
unnamed: QG1.2, mini_G1.1
unnamed: QG1.3, R2.2, SW_R_or_G1.1
unnamed: QR1.2, mini_R1.1
unnamed: QR1.3, R4.2, SW_R_or_G1.3
unnamed: QW1.1, R5.2
unnamed: QW1.2, SW_R_or_G1.2, SW_all1.2, W_light(-)1.1
unnamed: R1.1, mini_G1.2
unnamed: R1.2, pi_GPIO_(G+)1.1
unnamed: R2.1, RG_light_(-)1.2
unnamed: R3.1, pi_GPIO_(R+)1.1
unnamed: R3.2, mini_R1.2
unnamed: R4.1, RG_light_(-)1.1
unnamed: R5.1, pi_GPIO_(W+)1.1
unnamed: RV_white1.2, to_White(+)1.1

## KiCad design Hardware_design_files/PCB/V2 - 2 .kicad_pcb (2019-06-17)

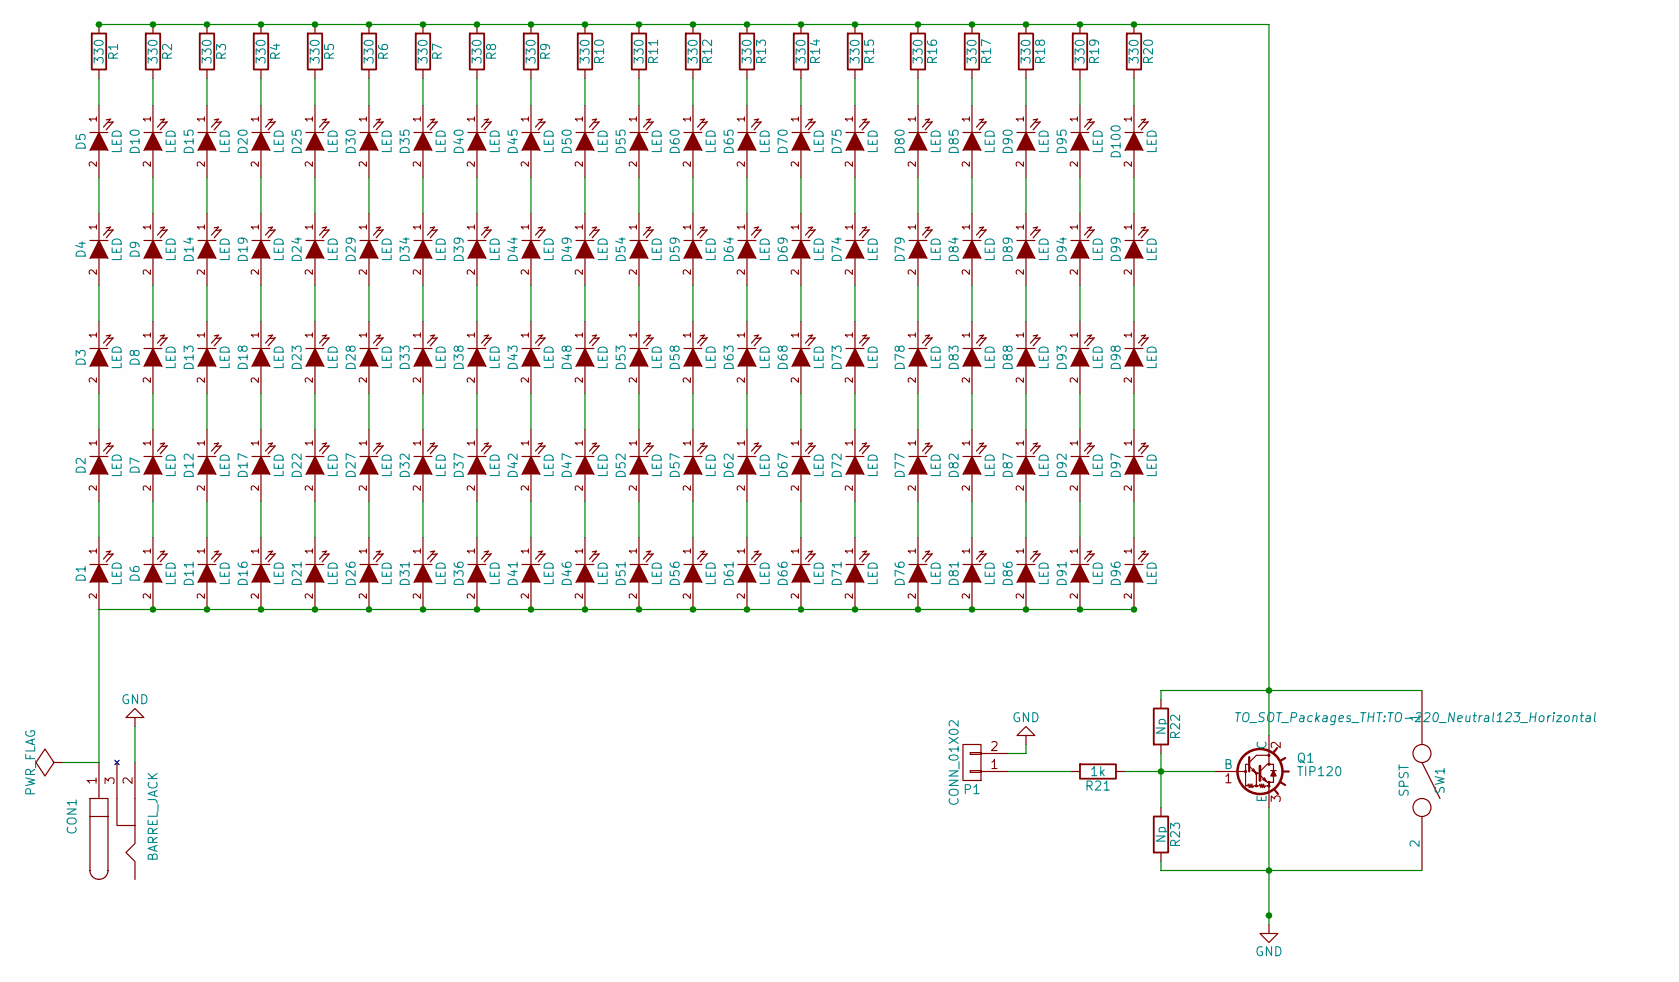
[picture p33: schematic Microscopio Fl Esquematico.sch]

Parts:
CON1: BARREL_JACK
D1, D2, D3, D4, D5, D6, D7, D8, D9, D10, D11, D12, D13, D14, D15, D16, D17, D18, D19, D20, D21, D22, D23, D24, D25, D26, D27, D28, D29, D30, D31, D32, D33, D34, D35, D36, D37, D38, D39, D40, D41, D42, D43, D44, D45, D46, D47, D48, D49, D50, D51, D52, D53, D54, D55, D56, D57, D58, D59, D60, D61, D62, D63, D64, D65, D66, D67, D68, D69, D70, D71, D72, D73, D74, D75, D76, D77, D78, D79, D80, D81, D82, D83, D84, D85, D86, D87, D88, D89, D90, D91, D92, D93, D94, D95, D96, D97, D98, D99, D100: LED; LED-5MM
P1: CONN_01X02; Pin_Header_Straight_1x02
Q1: TIP120; TO-220_Neutral123_Horizontal
R1, R2, R3, R4, R5, R6, R7, R8, R9, R10, R11, R12, R13, R14, R15, R16, R17, R18, R19, R20: 330; Resistor_Horizontal_RM7mm
R21: 1k; Resistor_Horizontal_RM7mm
R22, R23: Np; Resistor_Horizontal_RM7mm
SW1: SPST; SW_DIP_x1_Slide

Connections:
GND: CON1.2, P1.2, Q1.3 (E), R23.2, SW1.2
unnamed: CON1.1, D1.2 (A), D6.2 (A), D11.2 (A), D16.2 (A), D21.2 (A), D26.2 (A), D31.2 (A), D36.2 (A), D41.2 (A), D46.2 (A), D51.2 (A), D56.2 (A), D61.2 (A), D66.2 (A), D71.2 (A), D76.2 (A), D81.2 (A), D86.2 (A), D91.2 (A), D96.2 (A)
unnamed: D1.1 (K), D2.2 (A)
unnamed: D2.1 (K), D3.2 (A)
unnamed: D3.1 (K), D4.2 (A)
unnamed: D4.1 (K), D5.2 (A)
unnamed: D5.1 (K), R1.1
unnamed: D6.1 (K), D7.2 (A)
unnamed: D7.1 (K), D8.2 (A)
unnamed: D8.1 (K), D9.2 (A)
unnamed: D10.1 (K), R2.1
unnamed: D9.1 (K), D10.2 (A)
unnamed: D11.1 (K), D12.2 (A)
unnamed: D12.1 (K), D13.2 (A)
unnamed: D13.1 (K), D14.2 (A)
unnamed: D14.1 (K), D15.2 (A)
unnamed: D15.1 (K), R3.1
unnamed: D16.1 (K), D17.2 (A)
unnamed: D17.1 (K), D18.2 (A)
unnamed: D18.1 (K), D19.2 (A)
unnamed: D19.1 (K), D20.2 (A)
unnamed: D20.1 (K), R4.1
unnamed: D21.1 (K), D22.2 (A)
unnamed: D22.1 (K), D23.2 (A)
unnamed: D23.1 (K), D24.2 (A)
unnamed: D24.1 (K), D25.2 (A)
unnamed: D25.1 (K), R5.1
unnamed: D26.1 (K), D27.2 (A)
unnamed: D27.1 (K), D28.2 (A)
unnamed: D28.1 (K), D29.2 (A)
unnamed: D29.1 (K), D30.2 (A)
unnamed: D30.1 (K), R6.1
unnamed: D31.1 (K), D32.2 (A)
unnamed: D32.1 (K), D33.2 (A)
unnamed: D33.1 (K), D34.2 (A)
unnamed: D34.1 (K), D35.2 (A)
unnamed: D35.1 (K), R7.1
unnamed: D36.1 (K), D37.2 (A)
unnamed: D37.1 (K), D38.2 (A)
unnamed: D38.1 (K), D39.2 (A)
unnamed: D39.1 (K), D40.2 (A)
unnamed: D40.1 (K), R8.1
unnamed: D41.1 (K), D42.2 (A)
unnamed: D42.1 (K), D43.2 (A)
unnamed: D43.1 (K), D44.2 (A)
unnamed: D44.1 (K), D45.2 (A)
unnamed: D45.1 (K), R9.1
unnamed: D46.1 (K), D47.2 (A)
unnamed: D47.1 (K), D48.2 (A)
unnamed: D48.1 (K), D49.2 (A)
unnamed: D49.1 (K), D50.2 (A)
unnamed: D50.1 (K), R10.1
unnamed: D51.1 (K), D52.2 (A)
unnamed: D52.1 (K), D53.2 (A)
unnamed: D53.1 (K), D54.2 (A)
unnamed: D54.1 (K), D55.2 (A)
unnamed: D55.1 (K), R11.1
unnamed: D56.1 (K), D57.2 (A)
unnamed: D57.1 (K), D58.2 (A)
unnamed: D58.1 (K), D59.2 (A)
unnamed: D59.1 (K), D60.2 (A)
unnamed: D60.1 (K), R12.1
unnamed: D61.1 (K), D62.2 (A)
unnamed: D62.1 (K), D63.2 (A)
unnamed: D63.1 (K), D64.2 (A)
unnamed: D64.1 (K), D65.2 (A)
unnamed: D65.1 (K), R13.1
unnamed: D66.1 (K), D67.2 (A)
unnamed: D67.1 (K), D68.2 (A)
unnamed: D68.1 (K), D69.2 (A)
unnamed: D69.1 (K), D70.2 (A)
unnamed: D70.1 (K), R14.1
unnamed: D71.1 (K), D72.2 (A)
unnamed: D72.1 (K), D73.2 (A)
unnamed: D73.1 (K), D74.2 (A)
unnamed: D74.1 (K), D75.2 (A)
unnamed: D75.1 (K), R15.1
unnamed: D76.1 (K), D77.2 (A)
unnamed: D77.1 (K), D78.2 (A)
unnamed: D78.1 (K), D79.2 (A)
unnamed: D79.1 (K), D80.2 (A)
unnamed: D80.1 (K), R16.1
unnamed: D81.1 (K), D82.2 (A)
unnamed: D82.1 (K), D83.2 (A)
unnamed: D83.1 (K), D84.2 (A)
unnamed: D84.1 (K), D85.2 (A)
unnamed: D85.1 (K), R17.1
unnamed: D86.1 (K), D87.2 (A)
unnamed: D87.1 (K), D88.2 (A)
unnamed: D88.1 (K), D89.2 (A)
unnamed: D89.1 (K), D90.2 (A)
unnamed: D90.1 (K), R18.1
unnamed: D91.1 (K), D92.2 (A)
unnamed: D92.1 (K), D93.2 (A)
unnamed: D93.1 (K), D94.2 (A)
unnamed: D94.1 (K), D95.2 (A)
unnamed: D95.1 (K), R19.1
unnamed: D96.1 (K), D97.2 (A)
unnamed: D97.1 (K), D98.2 (A)
unnamed: D98.1 (K), D99.2 (A)
unnamed: D100.1 (K), R20.1
unnamed: D99.1 (K), D100.2 (A)
unnamed: P1.1, R21.2
unnamed: Q1.1 (B), R21.1, R22.2, R23.1
unnamed: Q1.2 (C), R1.2, R2.2, R3.2, R4.2, R5.2, R6.2, R7.2, R8.2, R9.2, R10.2, R11.2, R12.2, R13.2, R14.2, R15.2, R16.2, R17.2, R18.2, R19.2, R20.2, R22.1, SW1.1

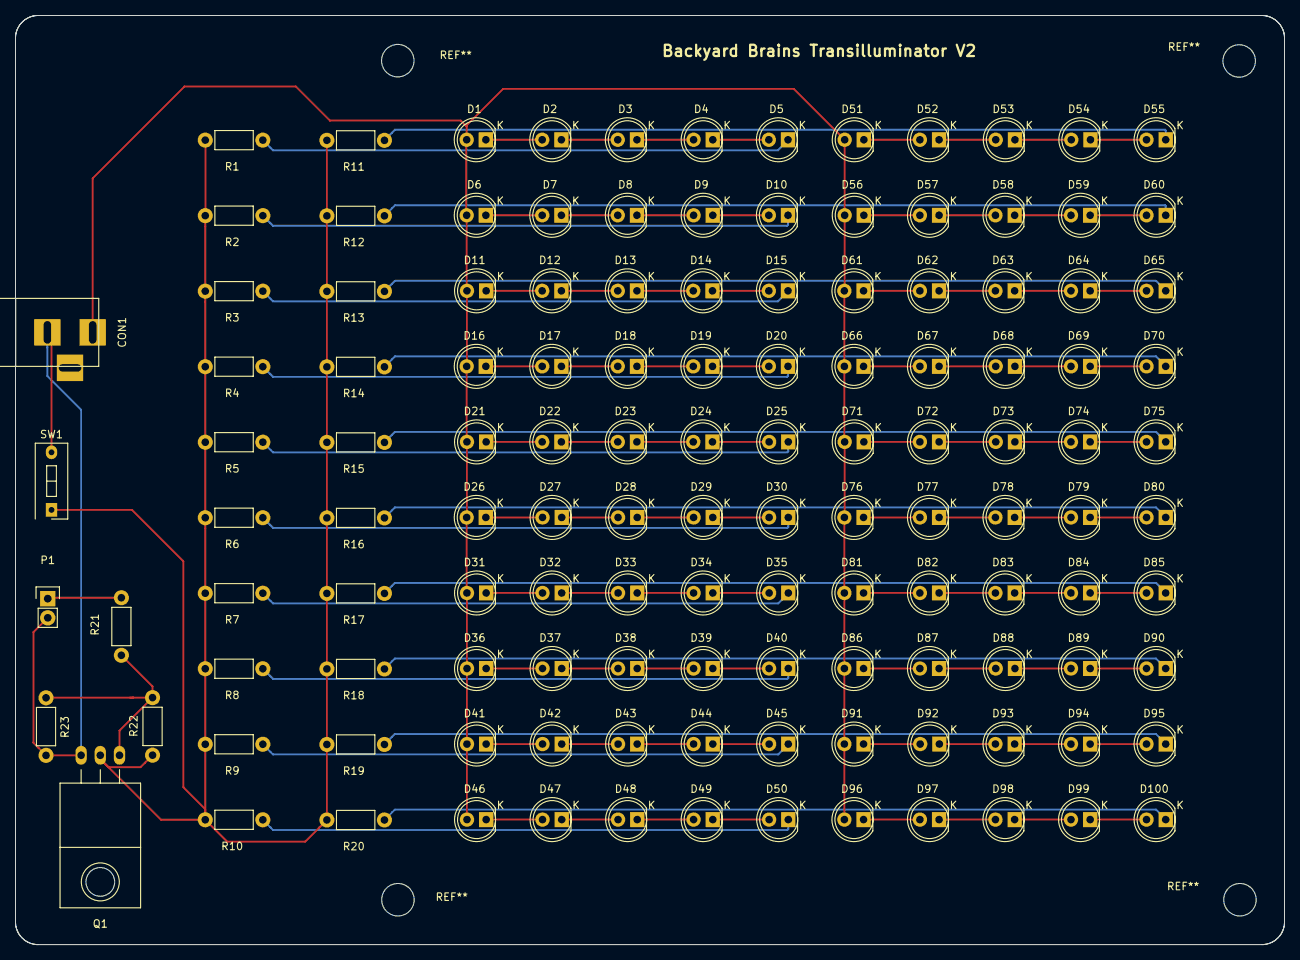
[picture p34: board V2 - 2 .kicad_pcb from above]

Board: 2 copper layers, 168.0 x 123.0 mm, 127 parts (0 on the bottom side), 105 nets.

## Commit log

2016-11-21 Update to newer code without previews and some better camera settings. Also attempt to use matplotlib in notebook.
2016-12-21 Timelapse with new settings for the camera
2017-01-29 Cut down to use on every 10th frame for speed. More comments. Plot outputs now back in notebook.
2017-03-06 2D Files
    Laser Cut Files for Production
2017-03-07 Create Assembly instructions
2017-03-12 pull design files
    [Microscopio Fl Esquemático.sch, V2 - 2 -B.Adhes.gbr, V2 - 2 -B.CrtYd.gbr, V2 - 2 -B.Cu.gbr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]
2017-03-20 Add files via upload
    Corrección de assembly instructions
2017-05-16 Upload assembly instructions for the top module.
2017-07-13 Simplify and cut down tutorial.
2017-07-14 Changing module name to lower case, first have to remove
2017-07-17 add new functions to save defined ROI frames and complete the analysis in the notebook usage example
2017-08-03 Add files for 3d printing
    [MF6-3 Final Cut - Cam Adapt.stl, MF6-3 Final Cut - Focus Knob.stl, MF6-3 Final Cut - Lock Knob.stl, MF6-3 Final Cut - Spacer L.stl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]
2017-08-21 Updated Authors
    [0-MF6-3 Final Cut - Paper Diffusor.dxf, 0-MF6-3 Final Cut - Raspberry Adaptor Acrilic.dxf, 0-MF6-3 Final Cut - Spacer L.stl, 0-MF6-3 Final Cut - Spacer R.stl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]
2017-08-31 Updated Assembly Instructions
2017-09-06 Replaced 3d files for printing
    [Focus Knob.stl, MF6-3 Final Cut - 3D Parts.stl, MF6-3 Final Cut - Raspberry Cam Adaptor.stl, MF6-3 Final Cut - Spacer L.stl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]
2017-09-08 reorganization of 2D and 3D files
    [3Dalltogether.stl, Focus Knob.stl, MF6-3 Final Cut - Dimensiones.dxf, MF6-3 Final Cut - Filter Amber Acrilic.dxf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]
2017-09-08 rename kicad files and assembly instructions
    [Microscopio Fl Esquematico.sch]
2017-09-08 Create folder for ready-to-cut files
2017-09-08 Added ready-to-cut files
    [Fluopi - Amber Ac - 3mm - 300x300 mm.dxf, Fluopi - Black Ac - 3mm - 800x500 mm.dxf, Fluopi - Blue Ac - 3mm - 300x300 mm.dxf, Fluopi - Paper Diffusor - 300x300 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]
2017-09-08 Create folder for ready to print files
2017-09-08 Added ready to print file for all the 3d parts
    [Fluopi - All 3D print parts.stl]
2017-09-09 cost breakdown file added
    [Cost_Breakdowm_Chile_Ref.xlsx]
2017-09-10 deleted repeated stl file
    [3Dalltogether.stl]
2017-09-13 Delete 0-0-0-0-0-0-0-0-5mm Blue LED - 470 nm - T1 3:4 LED w: 120 Degree Viewing Angle | Through Hole LEDs | Component LEDs | Super Bright LEDs.pdf
    name problems, I will fix and reload it
2017-09-13 Delete 0-0-0-0-0-0-0-5mm Blue LED - 470 nm - T1 3:4 LED w: 120 Degree Viewing Angle | Through Hole LEDs | Component LEDs | Super Bright LEDs.pdf
    filename problems, I will fix and reload it
2017-09-27 create the folder Hardware_control, add LED control files to that folder and move timelapase.py also
2017-10-06 make minor code corrections, clean some comments and specify the cycle printed information
2017-10-09 complete de example image data
2017-10-11 clarify some things on the notebook and eliminate some print from plotting
2017-10-30 Update timelapse.py
    Los dos puntos ":" usados en el time stamp del nombre de archivo no son válidos como nombre de archivo en sistemas no linux, así que se cambia por un guion bajo "_"
2018-03-13 a folder cotaning updates on design files, a doc with FAQs and openSCAD code
    [threads.scad]
2018-03-13 STLs and openscad files for new camera holder and M12 adapter
    [M12_mount_RPI_FF.scad, cam_holder.scad, cam_holder_V2_RPI_cam.stl, threads.scad]
2018-03-13 added link to README
    [threads.scad]
2018-05-29 acrylics chart for similar blue filters added
2018-10-08 moved positive track away from screw hole, so that the screw does not damage it when placed in
    [V2 - 2 -B.Adhes.gbr, V2 - 2 -B.CrtYd.gbr, V2 - 2 -B.Cu.gbr, V2 - 2 -B.Fab.gbr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]
2019-04-16 Add files via upload
    Increase the track width from 0.2 to 1.1. Also correct some mistakes in the track and the raspi conector fingerprint
    [V2 - 2 -B.Cu.gbr, V2 - 2 -B.Mask.gbr, V2 - 2 -B.SilkS.gbr, V2 - 2 -Edge.Cuts.gbr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]
2019-04-16 Add files via upload
    include a text file with manufacturing specifications (like material, thickness, etc)
2019-06-17 tl_roi function was corrected to avoid inconsistenses with time vector v/s frame. Also more functionatilities were added and some computing redundance was eliminated
2020-03-30 RPI camera M12 lenses mount design file and STL model was added
    [M12_RPIcam_mount.scad, M12_mount_RPI_FF.scad, cam_holder.scad, cam_holder_V2_RPI_cam.stl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]
2020-03-30 camera holder design file and STLs for RPIv2 and Waveshare cameras were added
    [Flat_cam_holder.scad, Flat_cam_holder_RPIV2cam.stl, Flat_cam_holder_WScam.stl]
2020-03-30 circular filter holder and focus knob adapted to attach it were added. It means both design files and STLs for 3D printing
    [Focus_knob_FilterAttach.scad, M12_focus_knob.stl, circle_filter_holder.scad, circle_filter_holder.stl]
2021-09-03 This is the FluOpti upgrade folder with all the code, designs and sample experiments
    [RG_Led_ring-B.Cu.gbr, RG_Led_ring-Edge.Cuts.gbr, RG_Led_ring-NPTH.drl, RG_Led_ring-PTH.drl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]
2023-12-30 update the filter to camera attach designs
    [Focus_knob_FilterAttach.scad, circle_filter_holder.scad]
